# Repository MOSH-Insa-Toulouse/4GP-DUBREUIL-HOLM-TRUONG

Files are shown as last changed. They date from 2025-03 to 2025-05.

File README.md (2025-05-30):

# 4GP-DUBREUIL-HOLM-TRUONG

## SMOMAIRE
- [I) Présentation](#Présentation)
- [II) Matériel necessaire](#Matériel-necessaire)
   - [Software](#Software)
   - [Hardware](#Hardware)
- [III)Livrables](#Livrables)
   - [1) Simulation LtSpice](#Simulation-LtSpice)
   - [2) Conception PCB avec KiCad](#Conception-PCB-avec-KiCad)
   - [3) Code Arduino](#Code-Arduino)
   - [4) Application Android avec MITApp Inventor](#Application-Android-avec-MITApp-Inventor)
   - [5) Réalisation Physique du Circuit](#Réalisation-Physique-du-Circuit)
   - [6) Banc de Test Expérimental](#Banc-de-Test-Expérimental)
- [IV)Gestion de projet](#gestion-projet)
   - [1)Répartition du travail](#repartition-travail)
   - [2) Contacts](#contacts)

## I) Présentation
Ce répertoire présente l'ensemble des éléments nécessaire à la conception d'un capteur de pression en graphite réalisé dans le cadre de l'UF I4GPMH21 : Du capteur au banc de test en open source hardware.
L’objectif était de concevoir un dispositif de mesure de déformation utilisant un capteur innovant, low-tech, basé sur du graphite appliqué sur papier, selon le principe décrit dans l’article scientifique :  
**"Pencil Drawn Strain Gauges and Chemiresistors on Paper"** (Cheng-Wei Lin, Zhibo Zhao, Jaemyung Kim & Jiaxing Huang). Ce capteur, d'une simplicité remarquable, est constitué d'un morceau de papier sur lequel du graphite est appliqué à l'aide d'un crayon à papier.



Le principe de fonctionnement repose sur l'observation que la déformation du papier entraîne une variation du nombre de particules de graphite interconnectées. Cette modification de la structure granulaire du graphite se traduit par une variation de la résistance et de la conductance du capteur. En exploitant cette propriété, il devient possible de remonter à la déformation subie, à l'instar d'une jauge de contrainte classique.



Le fonctionnement repose sur la variation de la conductivité électrique du graphite en fonction de la contrainte mécanique appliquée au support papier. Ce phénomène permet de mesurer la déformation avec une technologie simple, accessible et écologique.
## II) Matériel necessaire
### ***Software*** (Présenté dans l'ordre d'utilisation)
1. LtSpice : Logiciel permettant la modélisation et simulation des circuits électroniques. 
1. KiCad : Logiciel permettant le développement et conception du PCB (*Printed Board Circuit*)
1. Arduino IDE : IDE utilisé pour écrire le code du micro-contrôleur Arduino. 
1. MITApp Inventor : WebService pour le développement d'une application Android.
### ***Hardware***
1. Micro-contrôleur Arduino UNO
1. Modules 
    * Bluetooth HC-05
    * Capteur de déformation en graphite
    * Capteur de déformation du commerce
    * Écran OLED
    * Encodeur Rotatoire
    * Potentiomètre digital
    * Servo-Moteur
1. Banc de test réalisé à l'imprimante 3D

## III) Livrables
### 1) Simulation LtSpice

Un montage à transimpédance a été conçu afin d'amplifier le faible courant produit par le capteur graphite. Ce montage utilise un amplificateur opérationnel de précision (LTC1050) pour convertir le courant en tension, compatible avec les entrées analogiques d’un Arduino UNO.  

Trois filtres passe-bas ont été intégrés pour minimiser le bruit :
- Un filtre passe-bas passif (R1, C1) à l'entrée : filtre RC à 16 Hz pour réduire les perturbations en courant,
- Un filtre passe-bas actif (R3, C4) couplé à l'AOP : filtre actif à 1,6 Hz pour éliminer le bruit secteur (50 Hz),
- Un filtre passe-bas (R5, C2) à la sortie de l'AOP : filtre à 1,6 kHz pour lisser le signal final.

Des simulations transitoires et fréquentielles ont validé l’amplification et l’efficacité de la filtration (atténuation > 70 dB à 50 Hz).

#### ***Graphique***



#### ***Schéma du montage***


### 2) Conception PCB avec KiCad

Dans cette section, nous présentons le processus de conception du circuit imprimé du projet, allant de la simulation électrique à la modélisation 3D, en passant par le routage des composants. L’objectif est de réaliser une carte fonctionnelle permettant l’acquisition, le traitement et la transmission du signal mesuré par le capteur graphite.

### Étape 1 : Sélection et intégration des composants

Le circuit est conçu pour intégrer et connecter plusieurs composants essentiels à l’Arduino :

- Amplificateur opérationnel **LT1050** (amplification analogique du signal capteur)
- **Servomoteur** 
- **Potentiomètre numérique** (ajustement dynamique de gain)
- **Encodeur rotatoire**
- **Écran OLED**
- **Module Bluetooth HC-05** (communication sans fil avec une application mobile)
- Deux broches dédiées au **capteur graphène**

L’ensemble des connexions logiques et électriques est établi dans le schéma du PCB sur KiCad pour s'assurer de la compatibilité avec l’Arduino.

### Étape 2 : Simulation du schéma électrique

La conception a débuté par la création d’un schéma électrique simulé sous **LTspice**. Cette simulation permet de valider le comportement du circuit d’amplification, notamment autour de l’amplificateur opérationnel **LT 1050**, qui joue un rôle essentiel dans l’amplification du signal analogique issu du capteur graphite.

Une fois le schéma validé, il est reproduit dans **KiCad** afin de préparer la conception physique du circuit.

#### ***Schematic***



Ici sont présenté les différents éléments qui composeront le *shield* de notre projet ainsi que l'assignation des différentes connexions. On y retrouve en haut à droite l'ensemble des pins de connexion de l'arduino, à gauche, le schéma de l'amplificateur ainsi que la connexion du capteur graphène. Enfin, en bas, on retrouve la schématisation des différents modules à intégrer.

### Étape 3 : Routage PCB dans KiCad

La phase suivante consiste à réaliser le **routage** du circuit. Cela implique de placer les composants sur le PCB, de définir les couches, les largeurs de piste et les zones de masse, puis de relier chaque broche selon le schéma précédent.

L’objectif est d’optimiser la compacité, de limiter les interférences et d’assurer la robustesse du signal analogique.

**Aperçu du PCB routé :**




---

### Étape 4 : Visualisation 3D

Une fois le routage terminé, **KiCad** permet de générer un **modèle 3D** réaliste de la carte. Cette vue permet de vérifier l’encombrement, l’orientation des composants, et de prévoir les contraintes mécaniques ou d’intégration dans un boîtier physique.

**Modélisation 3D du PCB :**



---
### 3) Code Arduino
Le code Arduino doit permettre la réalisation des fonctions suivantes :
1. Récupérer les données du capteur graphène fait main
1. Naviguer dans un menu avec l'encodeur rotatoire et afficher sur l'écran OLED.
1. Gérer les valeurs de résistance du potentiomètre digital
1. Définir l'action du servo-moteur

Pour accomplir toutes ces actions, l'ensemble des fonctionnalités est géré à partir d'un menu à plusieurs niveau construit sur le modèle d'une machine à état.
Ainsi, dans le code deux fonctions sont construites pour gérer les mouvements de l'encodeur rotatoire et la gestion des menus.
L'arborescence finale du menu est construite comme suit : 
- Resistance R2
- Servo-moteur
   - Pousser
      - Angle 30
      - Angle 45
      - Angle 60
      - Angle 90
      - Retour
   - Tirer
      - Angle 30
      - Angle 45
      - Angle 60
      - Angle 90
      - Retour
   - Retour

Une fois l'angle selectionné, le mouvement du servo-moteur se déclenche et la mesure est réalisée (voir partie banc de test) 

---
### 4) Application Android avec MITApp Inventor

Nous avons développé une application Android avec **MIT App Inventor**. Cette application doit permettre la communication sans fil avec le module Bluetooth présent sur le *shield*, afin de visualiser les données du capteur en temps réel sur un téléphone android par exemple.

#### Objectifs

- Établir une connexion Bluetooth entre le smartphone Android et le module Arduino.
- Afficher la résistance du **potentiomètre digital** ainsi que celle du **capteur graphène**.
- Tracer une courbe en temps réel représentant l’évolution de la résistance du capteur.

#### Interface utilisateur

- Le bouton **Bluetooth** permet de se connecter au module Arduino via Bluetooth.
- Une fois connecté, le bouton change de couleur en **vert** et affiche l'état **Connected**.
- Pour se déconnecter, il suffit d'appuyer sur le bouton **Kicad**.
- Au centre de l'écran, un graphique affiche en temps réel la résistance mesurée du capteur graphène.
- En bas de l'écran, deux valeurs sont affichées :
  - La valeur de la résistance du **potentiomètre digital** séléctionnée
  - La valeur de la résistance instantanée du **capteur graphène**
 
  

#### Blocs MIT App Inventor

L'application utilise des blocs pour :

- Établir la connexion Bluetooth
- Recevoir les données depuis l'Arduino via UART
- Traiter les données reçues et les afficher dans un graphique
- Mettre à jour l'interface en fonction de l'état de la connexion

Voici une image représentant les blocs utilisés dans le projet :



---
### 5) Réalisation Physique du Circuit

Le circuit final a été soudé et testé dans les laboratoires du département. Des tests ont confirmé la stabilité du signal et l’efficacité des différents modules. Les soudures ont été réalisées manuellement pour garantir une bonne qualité de connexion.

---
### 6) Banc de Test Expérimental

Le banc de test qui nous a permis de réaliser l'expérience a été developpé avec le logiciel **Fusion 360**. 
Il est composé de :
1. Un support pour le micro-contrôleur Arduino
1. Un support pour le servo moteur
1. Un bras pour lié le servo-moteur au mobile
1. Un rail 
1. Un mobile 
1. Un support pour le capteur graphène.

L'ensemble de ces pièces sont à retrouver dans le dossier "Banc de test" ainsi que la vue globale présentée plus bas.

L'idée de ce banc de test est de courber le papier à l'aide du mobile qui sera actionner par le servo-moteur. Pour avoir un ensemble de mesure à réaliser le micro-contrôleur gère l'angle de la course imposé au moteur. Ainsi, on peut raisonnablement penser que pour un même angle de course appliqué, le capteur subira toujours la même déformation. 

Les courbes de mesure à établir seront donc la variation de résistance suivant la course faite par le mobile


Une fois le banc installé, il n'y a plus qu'à naviguer dans le menu affiché sur l'écran OLED à l'aide de l'encodeur rotatoire pour choisir la direction du mouvement et l'inclinaison. Une fois ces paramètres séléctionné par l'utilisateur, le resultat s'affiche dans le *Serial Monitor* ici Teleplot.


---
## Gestion du Projet
### 1) Répartition du travail
Au cours de ce projet, il a été necessaire de se répartir le travail pour couvrir le maximum de points importants. En cas de questions pour les futurs lecteurs ne pas hésiter à contacter les personnes sur leur différents points.
Ainsi, les tâches ont été réparties comme suit : 

- DUBREUIL Pierrick
   - KiCad : 
      - Réalisation du plans *schematic*
      - PCB : Correction d'empreintes + Routage des pistes
   - Banc de test 3D : 
      - Conception des différents éléments du banc sur Fusion 360
      - Impression des éléments du banc
   - Code Arduino : 
      - Construction du menu global
      - Gestion des commandes du servo-moteur
      - Acquisition des données du capteur graphène et affichage
- HOLM Ane-Marie
   - Développement du *front-end* de l'application Android
   - Rédaction de la *datasheet* du capteur
- TRUONG Nguyen 
   - KiCad :
      - Création d'empreintes PCB
      - Correction routage des pistes
      - Rendu 3D final
   - Code Arduino
      - Gestion de la résistance du potentiomètre digital
   - MITAPP :
      - Conception de l'application

---
### 2) Contacts
[DUBREUIL Pierrick](https://github.com/pierrickdubreuil17)(pdubreuil@insa-toulouse.fr)

[HOLM Anne-Marie](https://github.com/anemho)

[TRUONG Nguyen Gia Khanh](https://github.com/ntruonginsatls) (ntruong@insa-toulouse.fr)

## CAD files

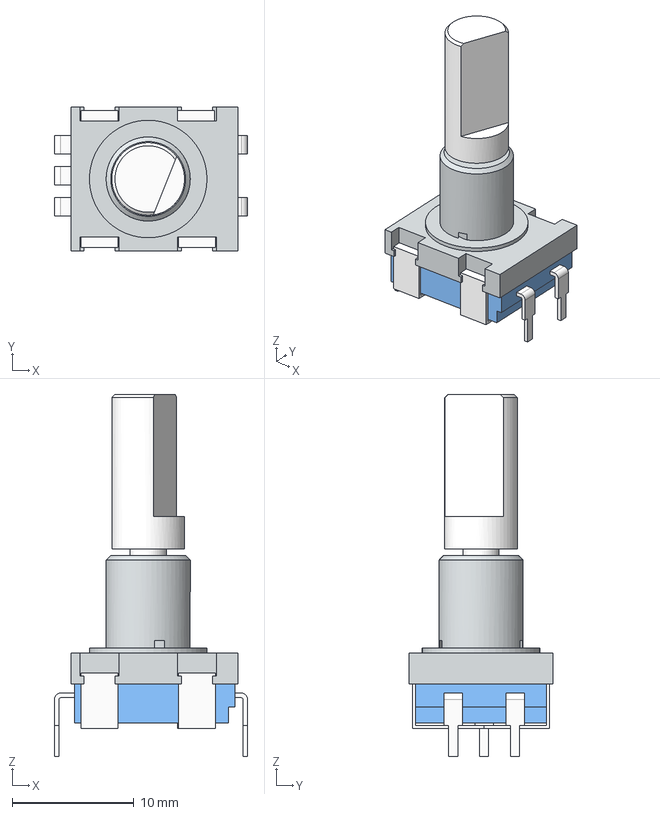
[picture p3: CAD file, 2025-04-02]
Module 3D/Encodeur rotatoire/Rotary Encoder without pcb Assembly.stp
15.8 x 11.8 x 29.7 mm
mtg flange
body_encoder
pins_encoder body_2 x 5
shaft_encoder

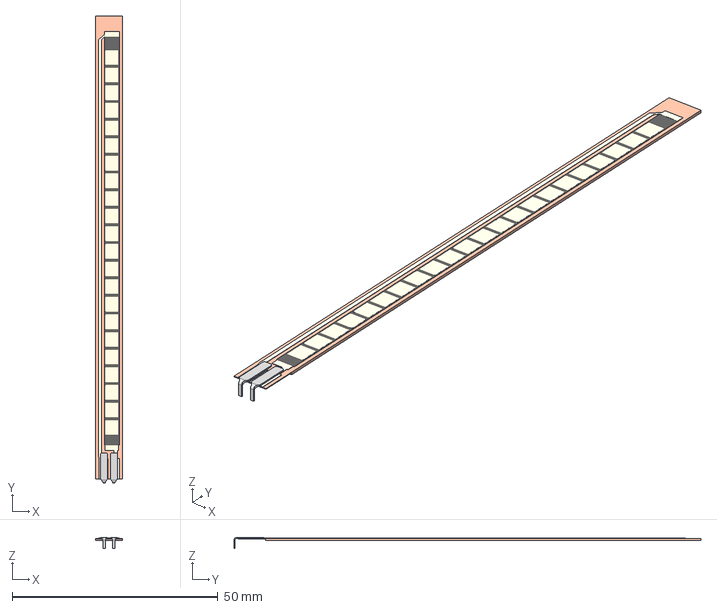
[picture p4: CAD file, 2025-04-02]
Module 3D/Flex Sensor/FS-L-0095-103-ST - Assembly.stp
6.45 x 113.5 x 2.77 mm
FS-L-0095-103-ST - Base
FS-L-0095-103-ST - Top

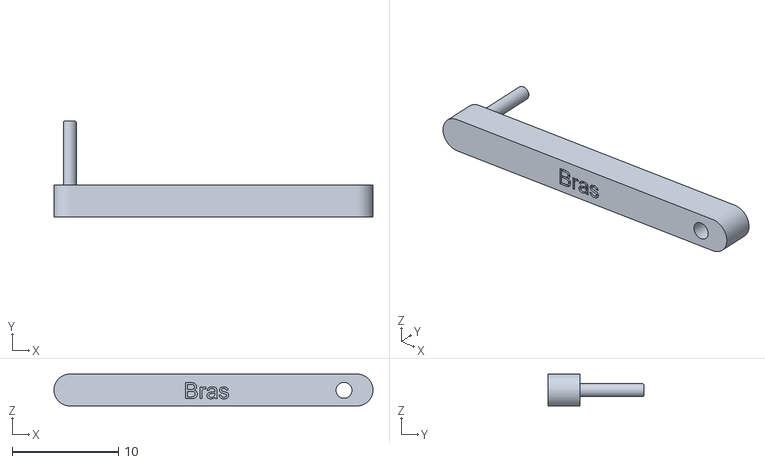
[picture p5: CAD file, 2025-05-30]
Banc de Test/Banc de test/Bras.stl
30.0 x 9.00 x 3.00

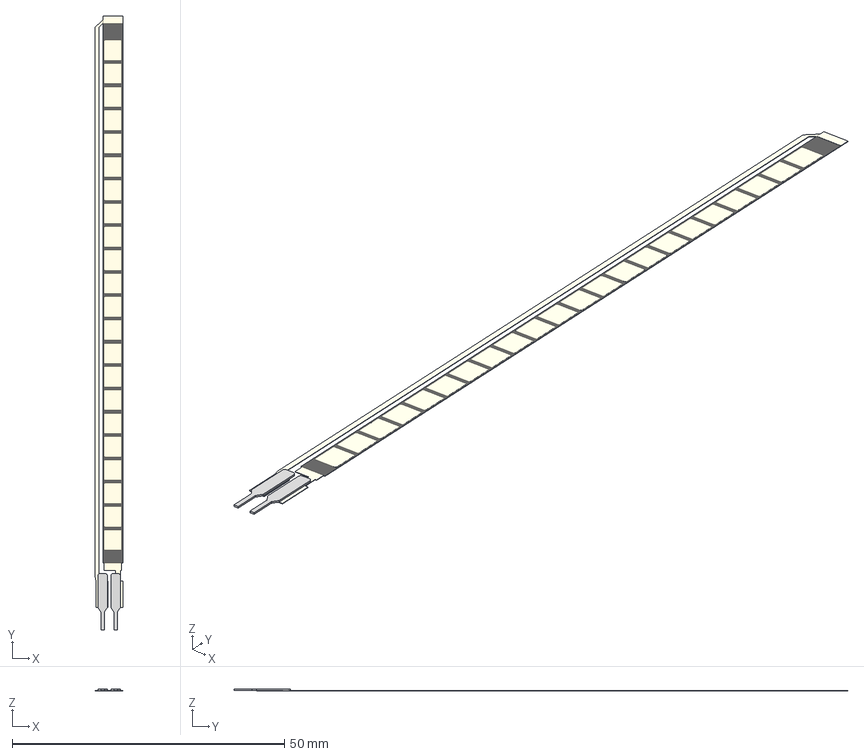
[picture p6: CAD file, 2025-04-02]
Module 3D/Flex Sensor/SolidEdge/FS-L-0095-103-ST - Top.stp
5.17 x 112.8 x 0.292 mm

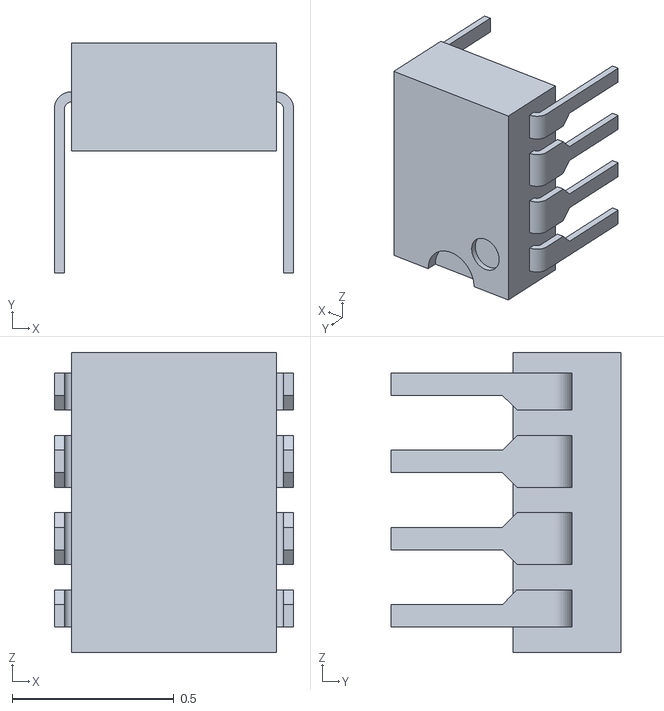
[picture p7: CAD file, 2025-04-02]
Module 3D/MCP/OP-AMPSTP_IGS.stl
0.741 x 0.712 x 0.928

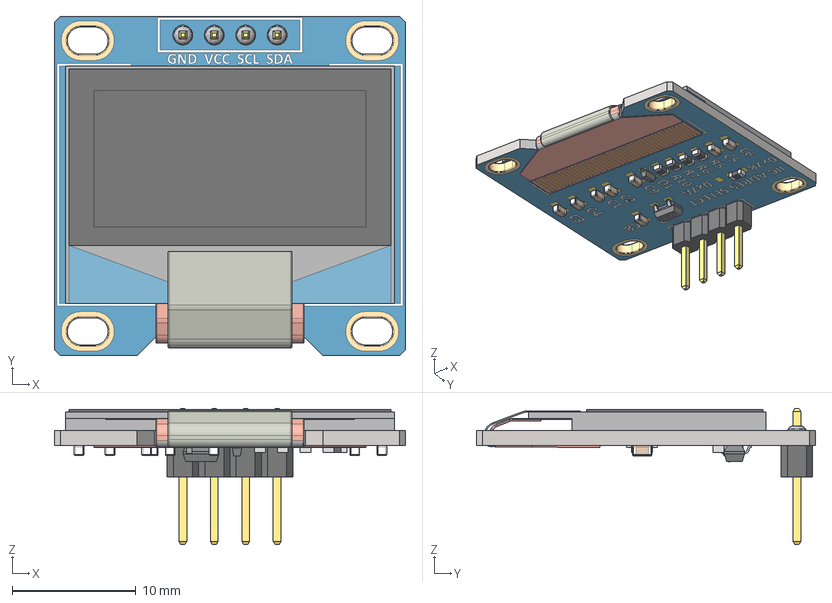
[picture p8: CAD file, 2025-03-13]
Module 3D/OLED/Pantalla OLED 0.96'' 128x64.stp
28.4 x 27.4 x 11.0 mm
SOT-23_TOR
RES_CR16_MTK_1 x 4
RES_CR16_MTK
SOD323F_DIO

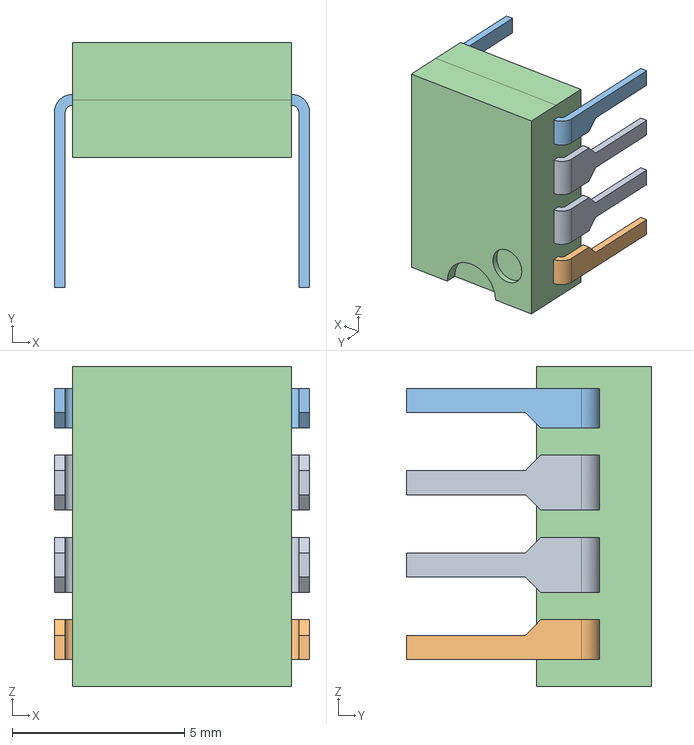
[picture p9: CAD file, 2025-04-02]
Module 3D/OP-AMP.stp
7.41 x 7.12 x 9.28 mm
Undefined x 9

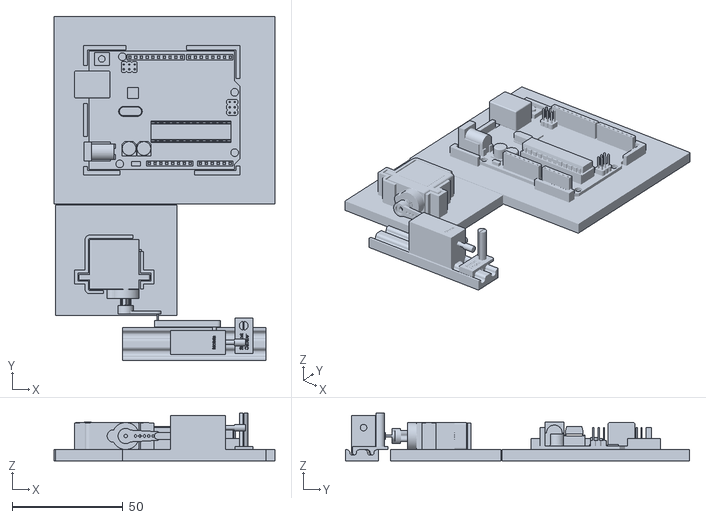
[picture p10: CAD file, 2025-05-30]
Banc de Test/Banc de test/Global.stl
100.0 x 155.8 x 21.5

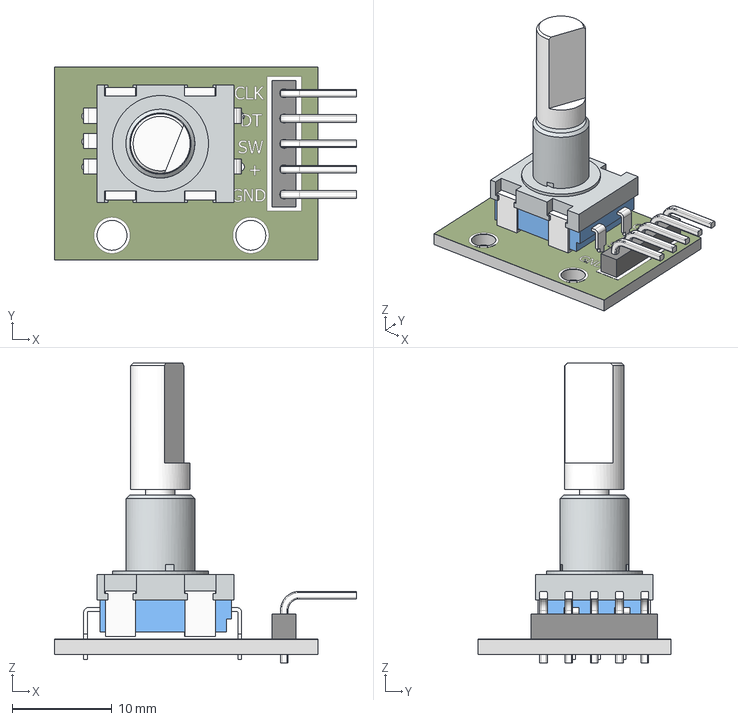
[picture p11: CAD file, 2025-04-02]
Module 3D/Encodeur rotatoire/rotary encoder_chesr_2013.stp
30.3 x 19.3 x 30.1 mm

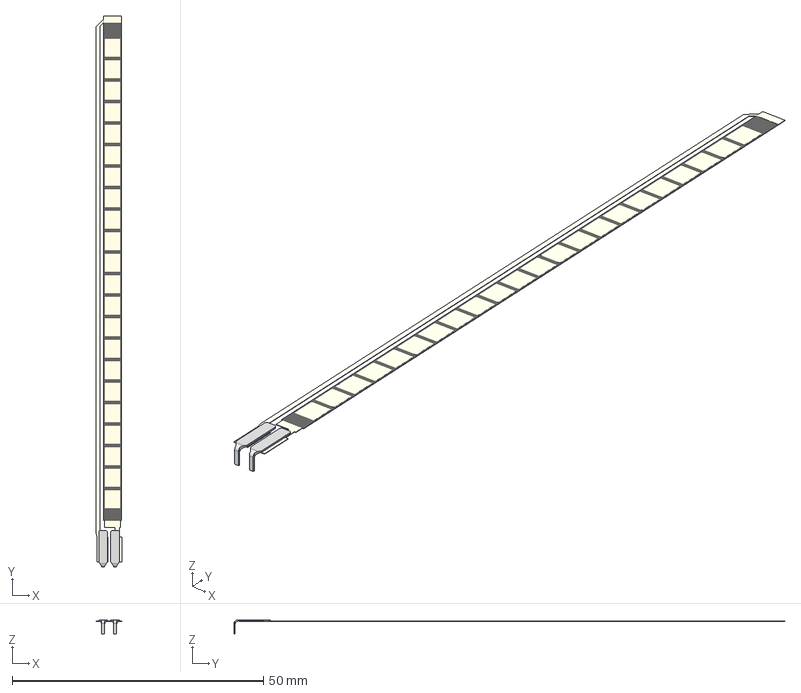
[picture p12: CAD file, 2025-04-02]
Module 3D/Flex Sensor/SolidEdge/FS-L-0095-103-ST - Top - Right.stp
5.17 x 109.7 x 2.77 mm

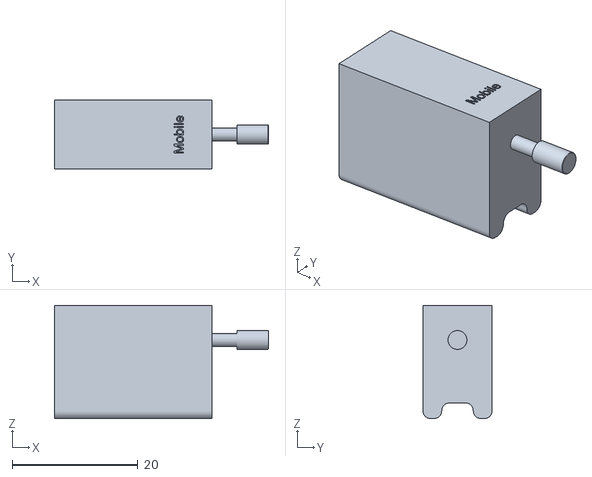
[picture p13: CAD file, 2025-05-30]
Banc de Test/Banc de test/Mobile.stl
34.0 x 11.0 x 18.0

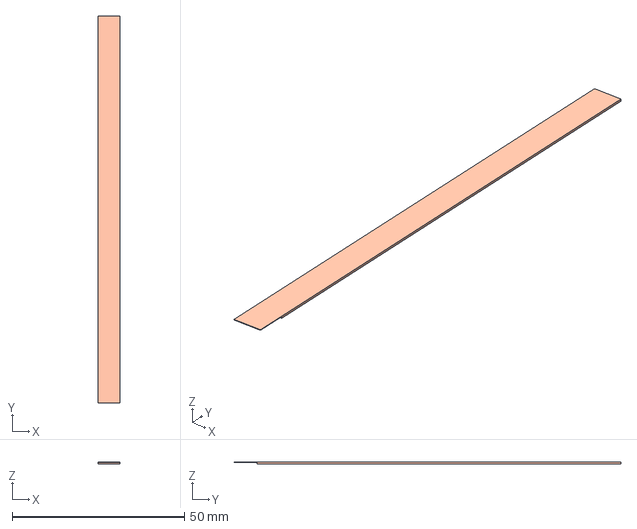
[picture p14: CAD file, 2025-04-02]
Module 3D/Flex Sensor/SolidEdge/FS-L-0095-103-ST - Base.stp
6.45 x 112.4 x 0.483 mm

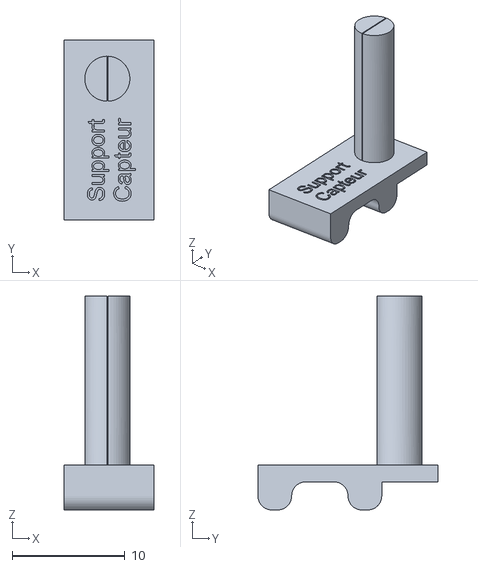
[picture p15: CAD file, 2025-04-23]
Banc de Test/Banc de test/Support Capteur.stl
8.00 x 16.0 x 19.0

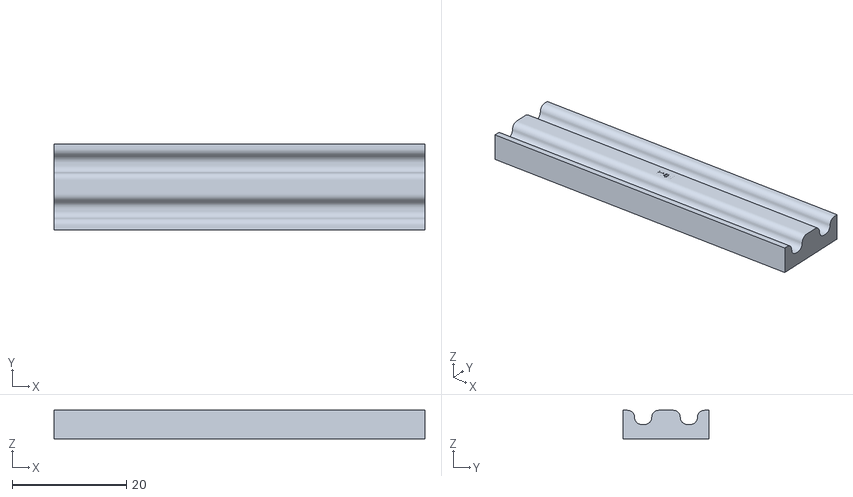
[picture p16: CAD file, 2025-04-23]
Banc de Test/Banc de test/Rail.stl
65.0 x 15.0 x 5.00

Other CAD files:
Banc de Test/Banc de test.dwg
Banc de Test/Banc de test/Support Arduino.stl
Banc de Test/Banc de test/Support Servo.stl

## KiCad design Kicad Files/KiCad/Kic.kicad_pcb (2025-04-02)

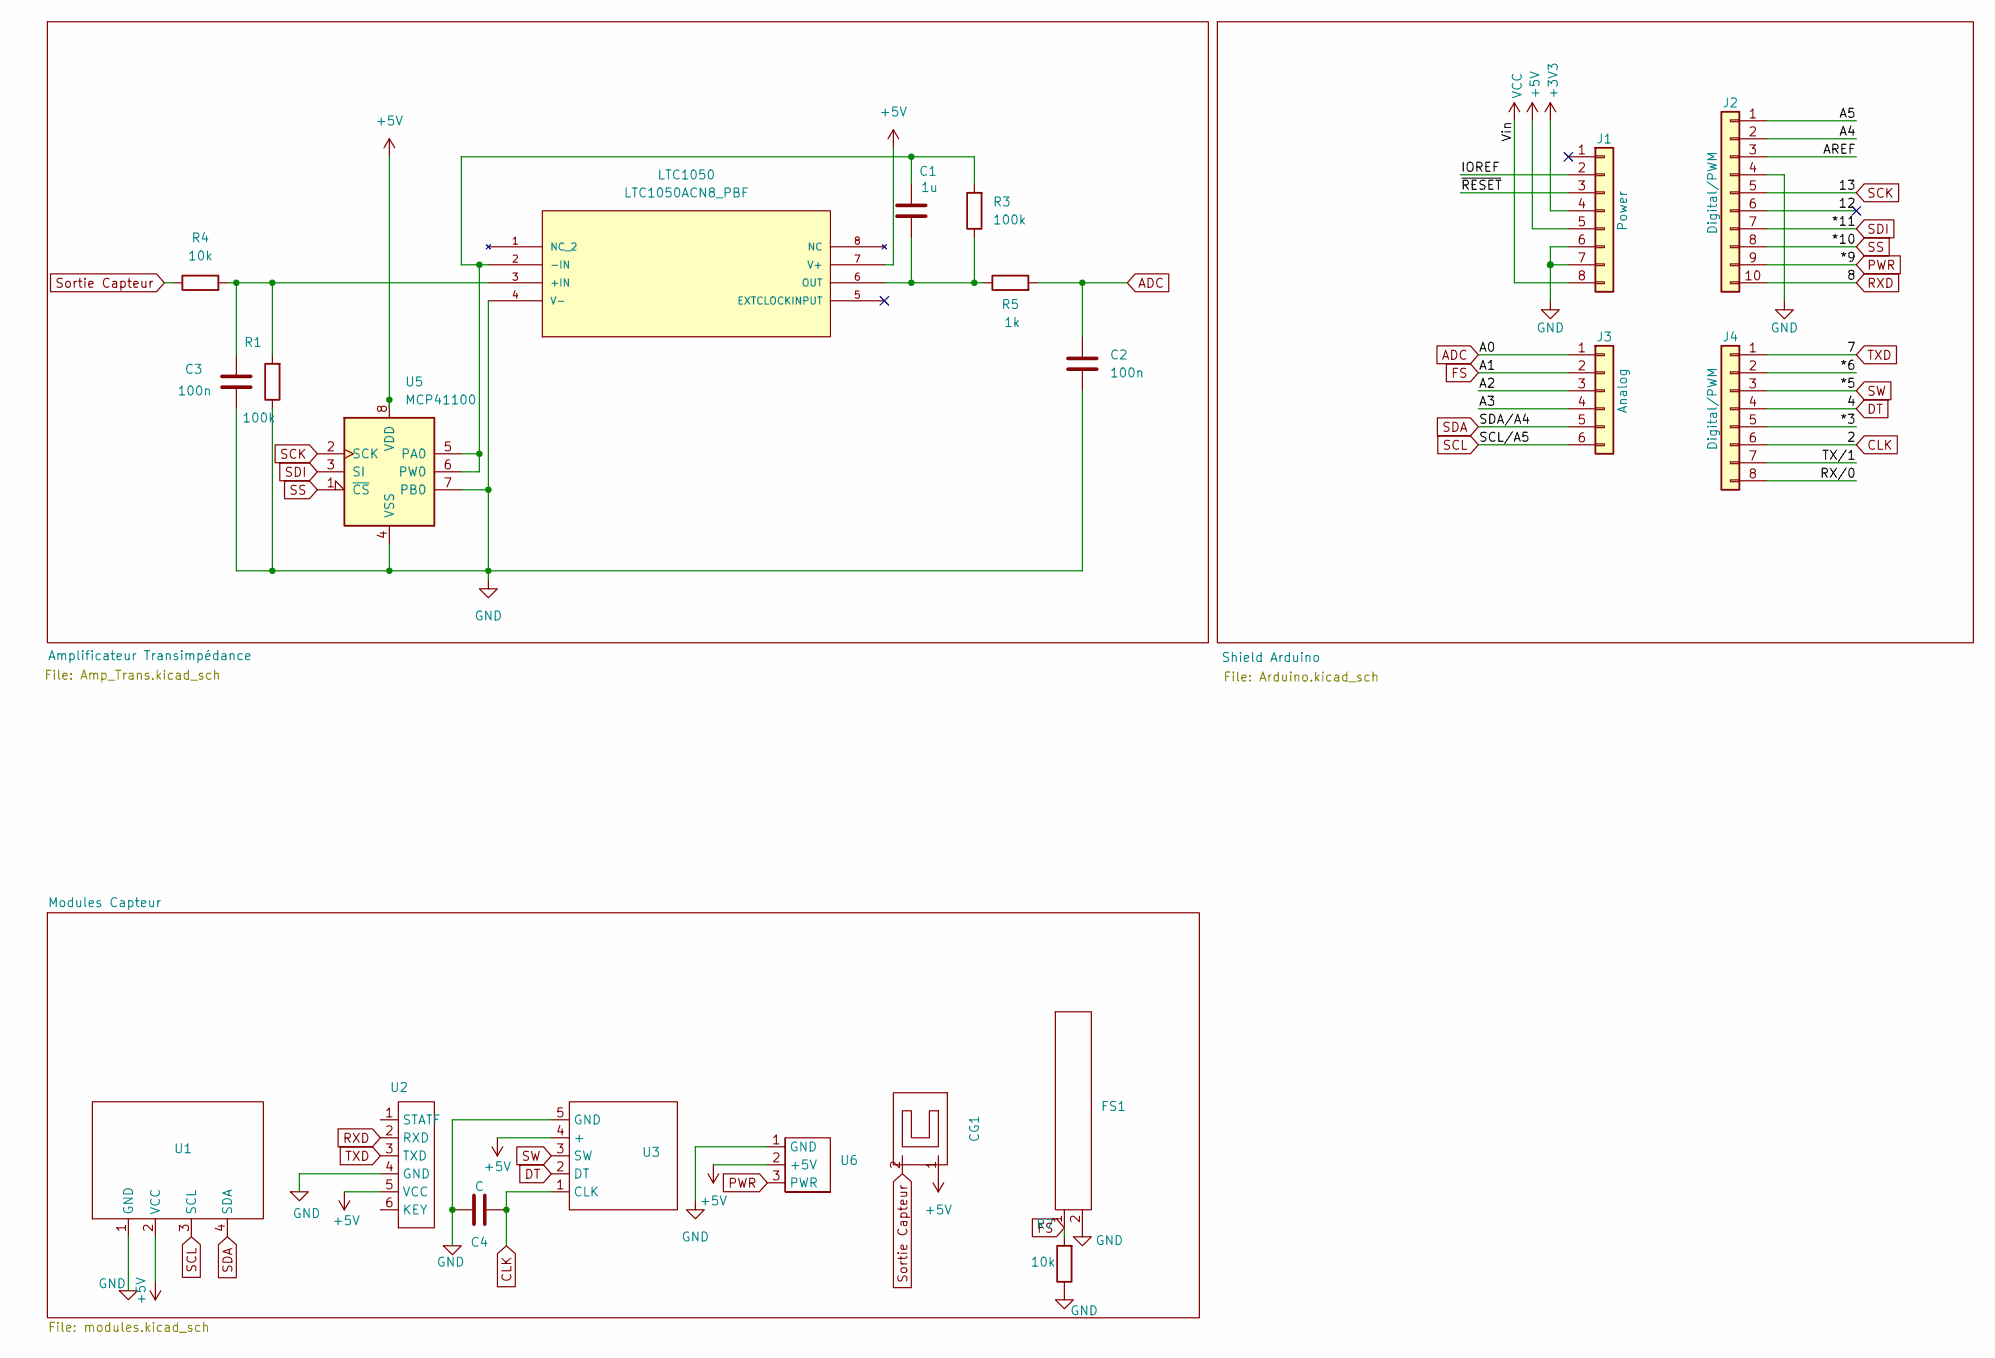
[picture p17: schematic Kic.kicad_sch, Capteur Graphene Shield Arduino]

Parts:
C1: 1u; C_Rect_L7.2mm_W5.5mm_P5.00mm_FKS2_FKP2_MKS2_MKP2
C2, C3: 100n; C_Disc_D4.3mm_W1.9mm_P5.00mm
C4: C; C_Disc_D4.3mm_W1.9mm_P5.00mm
CG1: SIP-2
FS1: SIP-2
J1: Power; PinSocket_1x08_P2.54mm_Vertical
J2: Digital/PWM; PinSocket_1x10_P2.54mm_Vertical
J3: Analog; PinSocket_1x06_P2.54mm_Vertical
J4: Digital/PWM; PinSocket_1x08_P2.54mm_Vertical
LTC1050: LTC1050ACN8_PBF; PDIP-8_N; MANUFACTURER_PART_NUMBER ltc1050acn8
R1, R3: 100k; R_Axial_DIN0204_L3.6mm_D1.6mm_P5.08mm_Horizontal
R4, R7: 10k; R_Axial_DIN0204_L3.6mm_D1.6mm_P5.08mm_Horizontal
R5: 1k; R_Axial_DIN0204_L3.6mm_D1.6mm_P5.08mm_Horizontal
U1: SIP-4
U2: BLUETOOTH2
U3: ENCODEUR ROTATION
U5: MCP41100; MCP4110
U6: ServomoteureHeader

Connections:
+3V3: J1.4
+5V: CG1.1, J1.5, LTC1050.7 (V+), U1.2 (VCC), U2.5 (VCC), U3.4 (+), U5.8 (VDD), U6.2 (+5V); also elsewhere on the board
/12: J2.6
/*3: J4.5
/*6: J4.2
/A2: J3.3
/A3: J3.4
/A4: J2.2
/A5: J2.1
/AREF: J2.3
/IOREF: J1.2
/RX/0: J4.8
/TX/1: J4.7
/~RESET: J1.3
ADC: C2.1, J3.1, R5.2
CLK: C4.2, J4.6, U3.1 (CLK); also elsewhere on the board
DT: J4.4, U3.2 (DT); also elsewhere on the board
FS: FS1.1, J3.2, R7.2
GND: C2.2, C3.1, C4.1, FS1.2, J1.6, J1.7, J2.4, LTC1050.4 (V-), R1.1, R7.1, U1.1 (GND), U2.4 (GND), U3.5 (GND), U5.4 (VSS), U5.7 (PB0), U6.1 (GND); also elsewhere on the board
unnamed: C3.2, LTC1050.3 (+IN), R1.2, R4.2
unnamed: C1.1, LTC1050.2 (-IN), R3.2, U5.5 (PA0), U5.6 (PW0)
unnamed: C1.2, LTC1050.6 (OUT), R3.1, R5.1
PWR: J2.9, U6.3 (PWR)
RXD: J2.10, U2.2 (RXD); also elsewhere on the board
SCK: J2.5, U5.2 (SCK)
SCL: J3.6, U1.3 (SCL)
SDA: J3.5, U1.4 (SDA)
SDI: J2.7, U5.3 (SI)
SS: J2.8, U5.1 (~CS)
SW: J4.3, U3.3 (SW); also elsewhere on the board
Sortie Capteur: CG1.2, R4.1
TXD: J4.1, U2.3 (TXD); also elsewhere on the board
VCC: J1.8

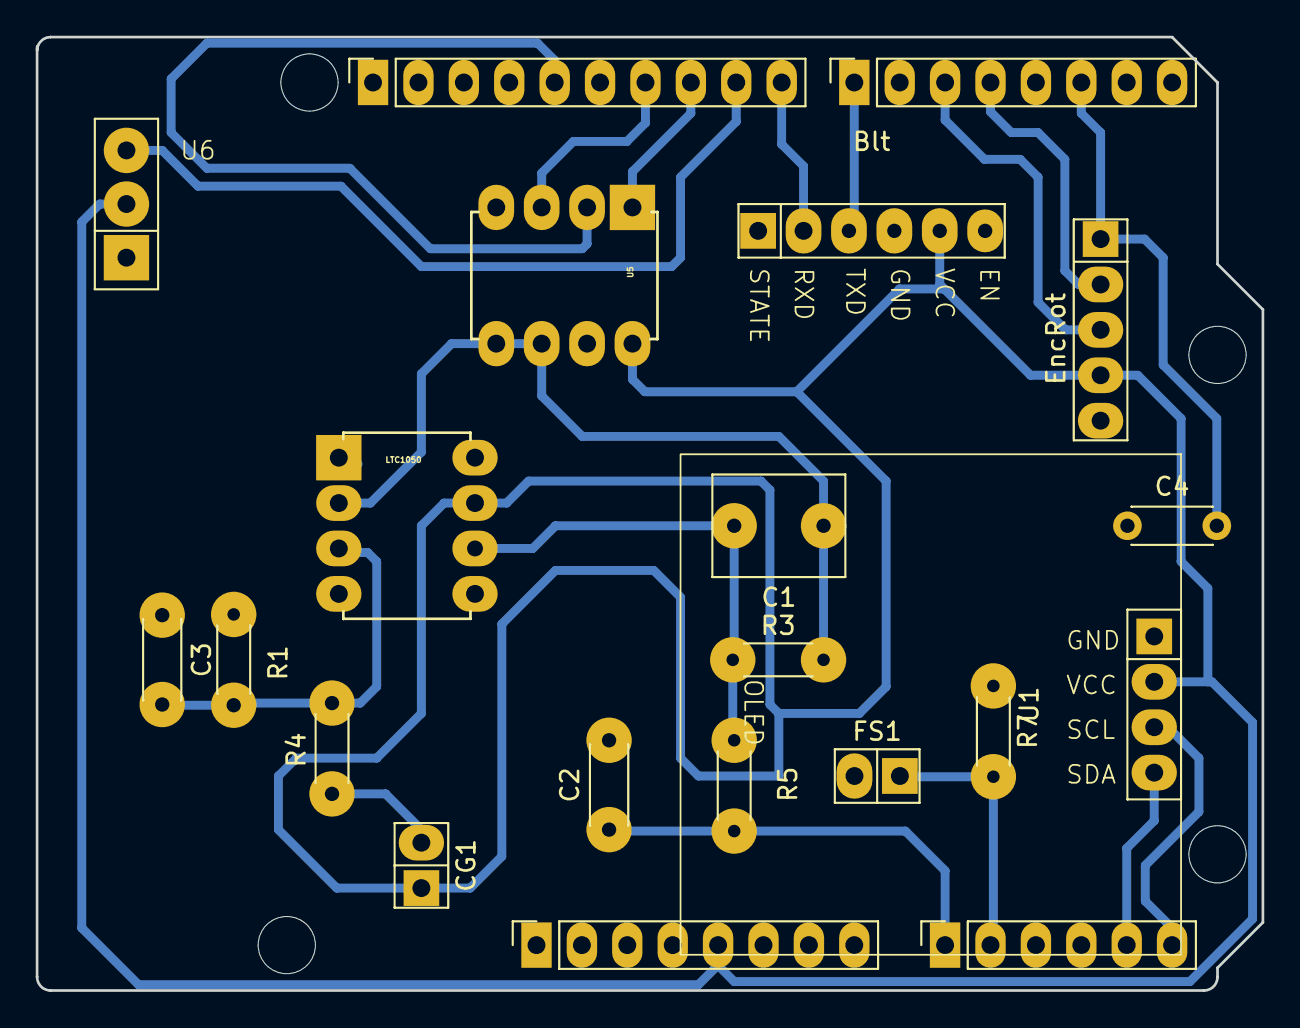
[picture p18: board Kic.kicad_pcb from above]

Board: 2 copper layers, 68.6 x 53.3 mm, 25 parts (0 on the bottom side), 19 nets.

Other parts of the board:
Blt: BLUETOOTH2
EncRot: ENCODEUR ROTATION
MH1, MH2, MH3, MH4: MountingHole_3.2mm

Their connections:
+5V: Blt.5 (VCC), EncRot.4 (+); also elsewhere on the board
CLK: EncRot.1 (CLK); also elsewhere on the board
DT: EncRot.2 (DT); also elsewhere on the board
GND: Blt.4 (GND), EncRot.5 (GND); also elsewhere on the board
RXD: Blt.2 (RXD); also elsewhere on the board
SW: EncRot.3 (SW); also elsewhere on the board
TXD: Blt.3 (TXD); also elsewhere on the board

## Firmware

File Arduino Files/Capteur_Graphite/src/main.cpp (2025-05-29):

#include <SPI.h>
#include <Wire.h>
#include <Adafruit_GFX.h>
#include <Adafruit_SSD1306.h>
#include <Servo.h>
#define SCREEN_WIDTH 128
#define SCREEN_HEIGHT 64
#define OLED_RESET    -1
#define SCREEN_ADDRESS 0x3C  // Adresse I2C de l'écran OLED
#define MAX_MESURE 10

enum MenuState{MAIN_MENU, SERVO_MENU, ANGLE_MENU};
MenuState currentMenu = MAIN_MENU;
unsigned long lastEncoderUpdate = 0;
const int ENCODER_STEP_DELAY = 150; // Délai entre chaque pas de l'encodeur
int lastEncoderPos = 0;

struct mesure{
  int angle;
  int valBrute;
  float tension;
};

mesure mesures[MAX_MESURE];
int currentMesure = 0;
bool finMesure = false;

// Initialisation des différents composants
Adafruit_SSD1306 ecranOLED(SCREEN_WIDTH, SCREEN_HEIGHT, &Wire, OLED_RESET); // Initialisation de l'écran OLED
Servo myservo; // Initialisation du servo-moteur
int pos = 90;
bool servoIsMoving = false; // État du mouvement du servo
unsigned long movestartTime = 0; // Temps de début du mouvement
const unsigned long moveDuration = 3000; // Durée du mouvement en millisecondes
int TargetPos = pos; // Position cible du servo

// Broches de connexion de l'encodeur
#define encoder0PinA  2  // CLK
#define encoder0PinB  4  // DT
#define ENCODER_SW    5  // bouton-poussoir

// Pin pour capteur graphène
#define GraphenePin A0 // Pin analogique pour le capteur de graphène

// Broches du MCP42100
const byte csPin           = 10;      // MCP42100 chip select pin
const int  maxPositions    = 256;     // Wiper can move from 0 to 255 = 256 positions
const long rAB             = 10000;   // 100k pot resistance between terminals A and B
const byte rWiper          = 125;     // 125 ohms pot wiper resistance
const byte pot0            = 0x11;    // Pot0 addr


//--------------------- Les Menus --------------------------------//

// Liste des éléments du menu principal
const char* menuItems[] = { "Resistance R2", "Servo-moteur" };
int menuIndex = 0;            // Index du menu actuel

// Sous-menu pour le servo-moteur
const char* menuItemsServo[] = { "Pousser", "Tirer", "Retour" };
int menuIndexServo = 0; // Index du sous-menu servo


const char* menuItemsAngle[] = { "Angle 30°", "Angle 45°", "Angle 60", "Angle 90", "Retour" };
int menuIndexAngle = 0; // Index du sous-menu angle

int SelectedDirection = 0; // Pousser ou Tirer


// Variables pour l'encodeur
int encoder0Pos = 0;          // Valeur de l'encodeur
bool adjustingResistance = false;  // État de l'ajustement de la résistance
bool buttonPressed = false;   // Variable pour vérifier l'état du bouton
 // État du sous-menu servo

// Ajout des différentes fonctions 

void showMenu() {
  static int lastIndex = -1;
  static bool lastAdjustState = false;
  
  if(menuIndex == lastIndex && adjustingResistance == lastAdjustState) return;

  ecranOLED.clearDisplay();

  if(adjustingResistance) {
    // Afficher seulement la résistance
    ecranOLED.setCursor(10, 10);
    ecranOLED.print("R: ");
    long resistanceWB = ((rAB * encoder0Pos) / maxPositions) + rWiper;
    ecranOLED.print(resistanceWB);
    ecranOLED.println(" ohms");
  }
  else {
    // Afficher le menu normal
    for (int i = 0; i < 2; i++) {
      ecranOLED.setTextColor(i == menuIndex ? SSD1306_BLACK : SSD1306_WHITE, 
                            i == menuIndex ? SSD1306_WHITE : SSD1306_BLACK);
      ecranOLED.setCursor(10, 10 + (i * 20));
      ecranOLED.println(menuItems[i]);
    }
  }

  ecranOLED.display();
  lastIndex = menuIndex;
  lastAdjustState = adjustingResistance;
}
// Affichage menu servo-moteur
void showServoMenu(){
  /**
   * @brief Affiche le sous-menu du servo-moteur sur l'écran OLED.
   * @param None
   * @return Aucun
   **/
ecranOLED.clearDisplay();
for(int i  = 0; i < 3; i++){
    if(i == menuIndexServo){
      ecranOLED.setTextColor(SSD1306_BLACK, SSD1306_WHITE);
    }else{
      ecranOLED.setTextColor(SSD1306_WHITE);
    }
    ecranOLED.setCursor(10, 10 + (i * 20));
    ecranOLED.println(menuItemsServo[i]);
  }
  ecranOLED.display();

}
// Fonction pour ajuster la valeur du potentiomètre
// Affichage du menu pour choix de l'angle
void showAngleMenu(){
  /**
   * @brief Affiche le sous-menu de sélection de l'angle sur l'écran OLED
   * @param None
   * @return aucun
   **/
  ecranOLED.clearDisplay();
  for(int i = 0; i < 5; i++){
    if(i == menuIndexAngle){
      ecranOLED.setTextColor(SSD1306_BLACK, SSD1306_WHITE);
    }else{
      ecranOLED.setTextColor(SSD1306_WHITE);
    }
    ecranOLED.setCursor(10, 10+(i*12));
    ecranOLED.println(menuItemsAngle[i]);
  }
  ecranOLED.display();
}

void setPotWiper(int addr, int pos) {
  digitalWrite(csPin, LOW);
  SPI.transfer(addr); // Envoyer l'adresse du potentiomètre
  SPI.transfer(pos);   // Envoyer la valeur du balai
  digitalWrite(csPin, HIGH);
}



int selectedAngle = 30;

void executeServoAction(){
  int angles[] = {30, 45, 60, 90};
  int baseAngle = angles[menuIndexAngle];

  int targetAngle = (SelectedDirection==0) ? 90-baseAngle : 90+baseAngle;
  targetAngle = constrain(targetAngle, 0, 180);
  myservo.write(targetAngle);
 delay(1000);
  // Mesure 1 s

  unsigned long debutMesure = millis();
  int samples = 0;
  long sumRaw = 0;
  int raw = analogRead(GraphenePin);
  while(millis()-debutMesure<1000){
    
    sumRaw +=raw;
    samples++;
    delay(300);
  }

  // Sauvegarde résultats

  mesures[currentMesure].angle = baseAngle;
  mesures[currentMesure].valBrute = sumRaw/samples;
  mesures[currentMesure].tension = raw * (5.0/1023.0); // Conversion en volts


  // Envoie des données au format csv
  Serial.print("Angle :");
  Serial.print(baseAngle);
  Serial.print(", Direction : ");
  Serial.print(SelectedDirection==0 ? "Pousser" : "Tirer");
  Serial.print(", Valeur brute :");
  Serial.print(mesures[currentMesure].valBrute);
  Serial.print(", Tension de Sortie :");
  Serial.println(mesures[currentMesure].tension);

  currentMesure = (currentMesure+1)%MAX_MESURE;

  // Retour position initiale

  myservo.write(90);
  servoIsMoving = true;
  movestartTime = millis();
  delay(500);  
  if(menuIndexAngle>=4) return;
}


void handleEncoderRotation() {
  if (millis() - lastEncoderUpdate < ENCODER_STEP_DELAY) return;

  int encoderDelta = 0;
  int currentStateA = digitalRead(encoder0PinA);
  int currentStateB = digitalRead(encoder0PinB);
  
  static int previousStateA = HIGH;
  if (previousStateA != currentStateA && currentStateA == LOW) {
    encoderDelta = (currentStateB == LOW) ? -1 : 1;
  }
  previousStateA = currentStateA;

  if (encoderDelta != 0) {
    lastEncoderUpdate = millis();
    
    if (adjustingResistance) {
      encoder0Pos = constrain(encoder0Pos + encoderDelta, 0, 255);
      setPotWiper(pot0, encoder0Pos);
      showMenu();
    } else {
      switch(currentMenu) {
        case MAIN_MENU:
          menuIndex = constrain(menuIndex + encoderDelta, 0, 1);
          showMenu();
          break;
          
        case SERVO_MENU:
          menuIndexServo = constrain(menuIndexServo + encoderDelta, 0, 2);
          showServoMenu();
          break;
          
        case ANGLE_MENU:
          menuIndexAngle = constrain(menuIndexAngle + encoderDelta, 0, 4);
          showAngleMenu();
          break;
      }
    }
  }
}


void handleMenuSelection() {
  switch (currentMenu) {
    case MAIN_MENU:
      if (menuIndex == 0) {
        adjustingResistance = !adjustingResistance;
        if (!adjustingResistance) showMenu(); // Rafraîchir seulement si on sort du mode réglage
      } else {
        currentMenu = SERVO_MENU;
        menuIndexServo = 0; // Réinitialiser la sélection servo
        showServoMenu();
      }
      break;

  case SERVO_MENU:
    if(menuIndexServo==2){
      currentMenu = MAIN_MENU;
      showMenu();
    }else{
      SelectedDirection = menuIndexServo;
      currentMenu = ANGLE_MENU;
      showAngleMenu();
    }
      break;
    case ANGLE_MENU:
    if(menuIndexAngle==4){
      currentMenu = SERVO_MENU;
      showServoMenu();
    }else{
      executeServoAction();
      currentMenu = ANGLE_MENU;
      showAngleMenu();
    }
    break;

    
  
  default:
    break;
  }
}
void afficherAction(String action){
  /**
   * @brief Affiche une action en cours sur l'écran OLED.
   * @param action : Action à afficher
   * @return Aucun
   **/

  ecranOLED.clearDisplay();
  ecranOLED.setCursor(10, 10);
  ecranOLED.print("En cours");
  ecranOLED.display();
  delay(300);
}



void measure(){
  /**
   * @brief Mesure la résistance à l'aide du capteur de graphène.
   * @param Aucun
   * @return Aucun
   **/
  Serial.println("Mesure en cours...");
  int sensorValue = analogRead(GraphenePin); // Lire la valeur du capteur
  float voltage = sensorValue * (5.0 / 1023.0); // Convertir la valeur en tension
  float resistance = (voltage * rAB) / (5.0 - voltage); // Calculer la résistance
  Serial.print("Résistance mesurée: ");
  Serial.print(resistance);
  Serial.println(" ohms");
  delay(300); // Attendre avant la prochaine mesure
}

void testCapteurGraphite() {
  // 1. Lire la valeur analogique brute
  int valeurBrute = analogRead(GraphenePin);
  
  // 2. Calculer la tension (pour info)
  float tension = valeurBrute * (5.0 / 1023.0);
  
  // 3. Afficher les résultats
  Serial.print("Valeur brute: ");
  Serial.print(valeurBrute);
  Serial.print(" | Tension: ");
  Serial.print(tension);
  Serial.println("V");
  
  // Petit délai pour lisibilité
  delay(500);
}
void setup() {
  Serial.begin(9600);

  pinMode(csPin, OUTPUT);           // Configure chip select as output
  pinMode(encoder0PinA, INPUT_PULLUP);
  pinMode(encoder0PinB, INPUT_PULLUP);
  pinMode(ENCODER_SW, INPUT_PULLUP);
  //attachInterrupt(0,doEncoder, RISING); // Interruption sur le changement d'état de l'encodeur
  // Initialiser le SPI
  digitalWrite(csPin, HIGH);        // Chip select default to de-selected
  SPI.begin();

  //Initialiser l'écran OLED
  if (!ecranOLED.begin(SSD1306_SWITCHCAPVCC, SCREEN_ADDRESS)) {
    Serial.println(F("OLED not found"));
    while (1);
  }

  ecranOLED.clearDisplay();
  ecranOLED.setTextSize(1);
  ecranOLED.setTextColor(SSD1306_WHITE);
  showMenu(); // Afficher le menu initial

  myservo.attach(9); // Attacher le servo à la broche 9
}

void loop() {

  setPotWiper(pot0,5);
  // Vérifier si le bouton est enfoncé
  if (digitalRead(ENCODER_SW) == LOW && !buttonPressed) {
    buttonPressed = true;
    handleMenuSelection();
    delay(150);
    }  // Marquer que le bouton a été enfoncé
   
   // Réinitialiser l'état du bouton lorsqu'il est relâché
  if (digitalRead(ENCODER_SW) == HIGH) {
    buttonPressed = false;
  }
  //---------- Navigation dans les menus
 handleEncoderRotation();
 
// Ajustement de la résistance avec l’encodeur
if (adjustingResistance && !servoIsMoving) {
  if (digitalRead(encoder0PinA) == LOW && digitalRead(encoder0PinB) == HIGH) {
    encoder0Pos = constrain(encoder0Pos + 1, 0, 255);
    setPotWiper(pot0, encoder0Pos);
    showMenu();  // Afficher la nouvelle valeur sur l'écran
  }

  if (digitalRead(encoder0PinA) == HIGH && digitalRead(encoder0PinB) == LOW) {
    encoder0Pos = constrain(encoder0Pos - 1, 0, 255);
    setPotWiper(pot0, encoder0Pos);
    showMenu();  // Afficher la nouvelle valeur sur l'écran
  }
}
}

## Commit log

2025-03-12 Test de commit 1
2025-03-12 Ajout des dossiers pour l'arborescence du projet
2025-03-12 Ajout de datasheet
2025-03-12 ajoute fichier KiCad
    [HC-05 Bluetooth Module.stp, HC05.SLDPRT, HC05.STEP, Pantalla OLED 0.96'' 128x64.stp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]
2025-03-13 Ajout des fichiers dans le dossier Kicad Files
    [Kic_V2.kicad_pcb]
2025-03-13 Nouvelle version des fichiers kicad
2025-03-13 Ajout du travail réalisé pendant la séance du 13.03+ Correction des pistes et ajout header servo-moteur
    [Amp_Trans.kicad_sch, Kic.kicad_pcb, Kic.kicad_sch, Kic_V2.kicad_pcb]
2025-03-16 Ajout d'une V5 des fichiers Kicadet mise à jour du fichier Arduino avvec l'ajout de code pour les différents modules
    [Amp_Trans.kicad_sch, Kic.kicad_pcb, Kic.kicad_sch]
2025-03-16 Ajout des bibliothèques perso de Pierrick et déplacement des bibliothèques de Nguyen dans le dossier Kicad files
2025-03-17 Modification d'attribution de pins
    [Amp_Trans.kicad_sch, Arduino.kicad_sch, Kic.kicad_pcb, Kic.kicad_sch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]
2025-03-21 Ajout de la nouvelle version du PCB
    [Amp_Trans.kicad_sch, Arduino.kicad_sch, KiCad V3.kicad_pcb, KiCad V3.kicad_sch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]
2025-03-22 Retravaille des pistes du PCB : Pose d'un via et vérification du plan de masse
    [Amp_Trans.kicad_sch, Arduino.kicad_sch, KiCad V3.kicad_pcb, KiCad V3.kicad_sch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]
2025-03-22 Ajout de .DS_Store dans .gitignore
2025-03-22 Suppression de .DS_Store du dépôt
2025-03-22 Ajout de .DS_Store dans .gitignore et suppression du suivi
2025-03-25 Modification des dossiers suite à la réalisation du PCB
    [Amp_Trans.kicad_sch, Arduino.kicad_sch, KiCad V3.kicad_pcb, KiCad V3.kicad_sch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]
2025-03-25 Modification du dossier Module 3D
    [HC-05 Bluetooth Module.stp, HC05.SLDPRT, HC05.STEP, Kic.kicad_pcb]
2025-03-25 Modification du fichier Readme.md
    [Banc de test.dwg]
2025-03-25 Ajout de la section "Arduino" dans le Readme.md
2025-03-25 Modification de la section "Contacts"
2025-03-27 Ajout image Kicad
    [Kic.kicad_pcb]
2025-03-27 Ajout du texte Arduino dans le Readme
2025-03-28 Changement dans la rubrique contact du Readme
2025-04-02 Ajout de la fonction de lecture du capteur dans l'arduino + Suppression de fichiers doublons
    [FS-L-0095-103-ST - Assembly.stp, FS-L-0095-103-ST - Base.stp, FS-L-0095-103-ST - Top - Right.stp, FS-L-0095-103-ST - Top.stp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]
2025-04-03 mettre a jour code arduino
2025-04-23 Mise à jour du code arduino
2025-04-23 Ajout de docstrings
2025-04-23 Ajout de docstring
2025-04-23 Mise au propre du dossier Arduino Files
2025-04-23 Suppression des doublons
2025-04-23 Ajouts des fichiers 3D pour le band de Test
    [Bras.stl, Global v10.stl, Mobile v3.stl, Rail v4.stl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]
2025-05-20 Modification du code arduino
2025-05-20 Fin de la fonction de navigation pour le servo moteur
2025-05-22 Fin code arduino
    [test.csv, test_donnée_capteur.csv]
2025-05-29 Mise à jour du Read.me + ajout du dossier contenant les documents pour la soutenance finale
2025-05-29 Ajout de l'image banc de test dans le readme
2025-05-30 Ajout du descriptif des fonction du code dans le readme
2025-05-30 Mise au propre des fichiers Github
    [Amp_Trans.kicad_sch, Arduino.kicad_sch, Bras.stl, Global v10.stl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]
2025-05-30 Ajout de la section Répartition du travail

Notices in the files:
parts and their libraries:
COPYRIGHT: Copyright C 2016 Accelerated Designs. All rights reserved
